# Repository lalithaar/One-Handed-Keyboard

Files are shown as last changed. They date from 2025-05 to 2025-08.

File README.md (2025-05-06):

# **One-Handed Keyboard**

> 我们收到了一封特殊的邮件。来信者的女儿在上学途中不幸遭到重型卡车碾压，右手永久失去了功能，用电脑的时候手得在键盘和鼠标之间频繁切换，打字很慢，很累。他想让我们帮他女儿做一个单手键盘。

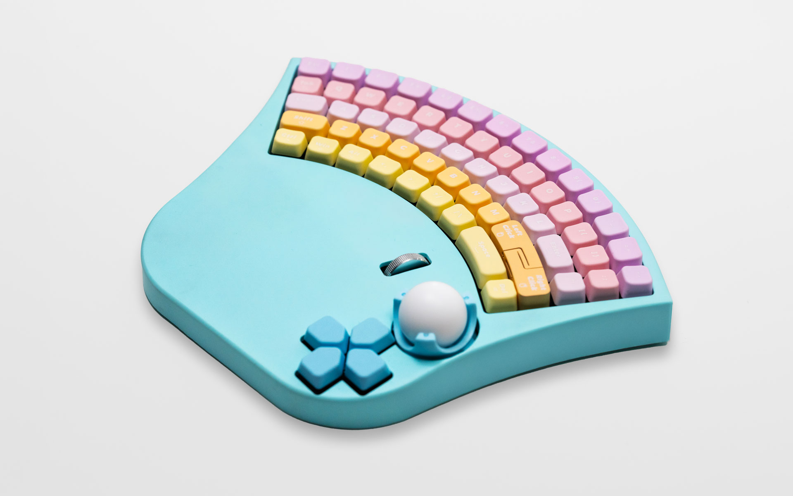
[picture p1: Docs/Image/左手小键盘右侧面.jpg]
左手小键盘


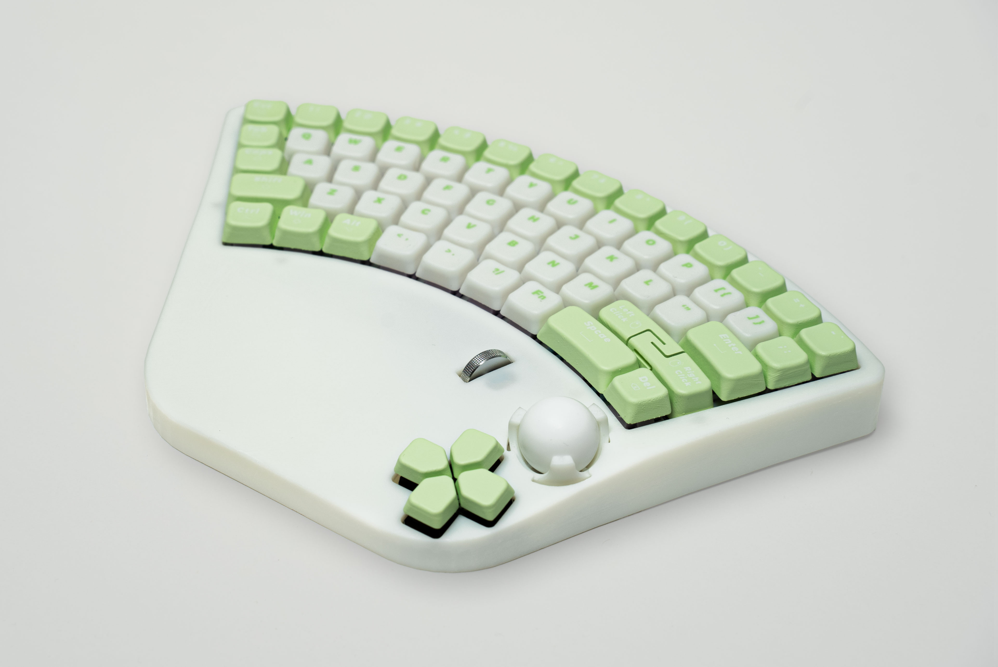
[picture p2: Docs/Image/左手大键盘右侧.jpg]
左手大键盘


这是一把单模且集成了轨迹球的机械键盘，固件使用[QMK](https://github.com/qmk/qmk_firmware)，感谢所有为 QMK 社区做出贡献的开发者。

键盘制作参考：[【何同学】我们做了个特别的键盘…](https://www.bilibili.com/video/BV1DtjAzUEb9)

硬件开源：[HTXStudio单手键盘](https://oshwhub.com/htx-studio/One-Handed_Keyboard)

[GitHub repository](https://github.com/htx-studio/One-Handed-Keyboard)

[Gitee repository](https://gitee.com/htxstudio/one-handed-keyboard)

开发环境与搭建参考[这里](https://docs.qmk.fm/newbs_getting_started "设置您的QMK环境")，固件源码在[这里](https://github.com/htx-studio/qmk_firmware/tree/master/keyboards/htx_studio)。

本仓库的资料内容包括：

* 左右手一共三款键盘的8块PCB，提供立创EDA工程。
* VIA改键配置文件，以及编译完成的固件。
* 模型设计文件。

---

## 仓库目录结构

#### Docs（文档）

芯片的数据手册与图片。

#### Firmware（固件）

三款不同型号键盘的QMK固件，以及用于VIA改键的JSON文件。

#### Hardware（硬件）

嘉立创EDA的项目文件。

#### Model（模型）

每个型号键盘使用到的模型文件，加工文件。

---

## 制作指南

### PCB：

1-右手键盘-热插拔(大)：板材FR-4，板厚1.6mm，四层板，层压结构JLC04161H-3313，阻抗管控+/-20%。

1-左手键盘-焊板(小)：板材FR-4，板厚1.6mm，双层板，ALPS黄轴插入时需稍用力安装到位。

1-左手键盘-热插拔(大)：板材FR-4，板厚1.6mm，四层板，层压结构JLC04161H-3313，阻抗管控+/-20%。

2-TypeC：板材FR-4，板厚1.6mm，双层板，标识CON1（仅适用于大键盘）。

3-轨迹球：板材FR-4，板厚1.6mm，双层板，模块需注意焊接方向，标识CON3。

4-鼠标滚轮：板材FR-4，板厚1.6mm，双层板，建议使用7mm高编码器，6mm高按键，按键触发压力≤180g，标识CON2。

5-方向按键：板材FR-4，板厚1.6mm，双层板，ALPS黄轴插入时需稍用力安装到位，标识CON4。

6-主控板-左手(小)：板材FR-4，板厚1.6mm，双层板。

> * 其中3款为键盘控制公用小板 `《3-轨迹球》《4-鼠标滚轮》《5-方向按键》`。
> * `《5-方向按键》`和 `《1-左手键盘-焊板(小)》`，按键轴使用ALPS黄轴。
> * 注意左右手大键盘并非完全镜像。
> * 轨迹球控制使用SPI1通道，滚轮有单独两条信号线，这可以使得替换其它控制设备而不需要较大的调整。
> * 主控使用 STM32G431CBU6。
> * 兼容A to C 或 C to C 数据线。

### 打印件：

键帽：树脂、PLA等。

轨迹球座：树脂、PLA等。

鼠标左右键：树脂、PLA等。

外壳：树脂、PLA等。

底座：树脂、PLA等。

### 加工：

定位板：推荐材料pom，厚1.5mm。

定位板棉条：单面留胶。

夹心棉：推荐材料poron，厚3.5mm。

轴座棉：厚2mm。

底棉：推荐材料poron，厚4mm。

硅胶垫（仅小键盘使用）：厚5mm，硬度Shore 00-10。

### 五金：

|                    | 大键盘用量（颗） | 小键盘用量（颗） |
| :----------------- | :--------------: | :--------------: |
| M3×3×4热熔铜螺母 |        8        |        8        |
| M2×2×3热熔铜螺母 |        2        |        -        |
| M2×3×3热熔铜螺母 |        17        |        12        |
| M3×6沉头螺丝      |        2        |        6        |
| M3×15沉头螺丝     |        -        |        4        |
| M3×22沉头螺丝     |        6        |        -        |
| M2×8杯头螺丝      |        4        |        4        |
| M2×3杯头螺丝      |        2        |        -        |
| M2×5杯头螺丝      |        13        |        8        |
| M3×16扁头螺丝     |        -        |        2        |

### 其它：

轨迹球：直径25mm，材质PTFE。

润滑球：直径2mm，材质PTFE，安装于打印件轨迹球座中，数量6颗。

滚轮：推荐直径19mm-20mm之间，厚4mm-5mm之间，材质金属。

卫星轴：2U钢板卫星轴。

按键轴：小键盘57颗超小ALPS黄轴，大键盘57颗常见机械轴。

排线：间距0.5mm，8P反向，10cm2条，15cm2条。

> * 控制板和小板的FPC座均有CON标识，对应接口相接。
> * 文件内使用可上下接FPC排线座，需要注意排线座均下接的情况下，使用反向排线连接。

### 模型结构：

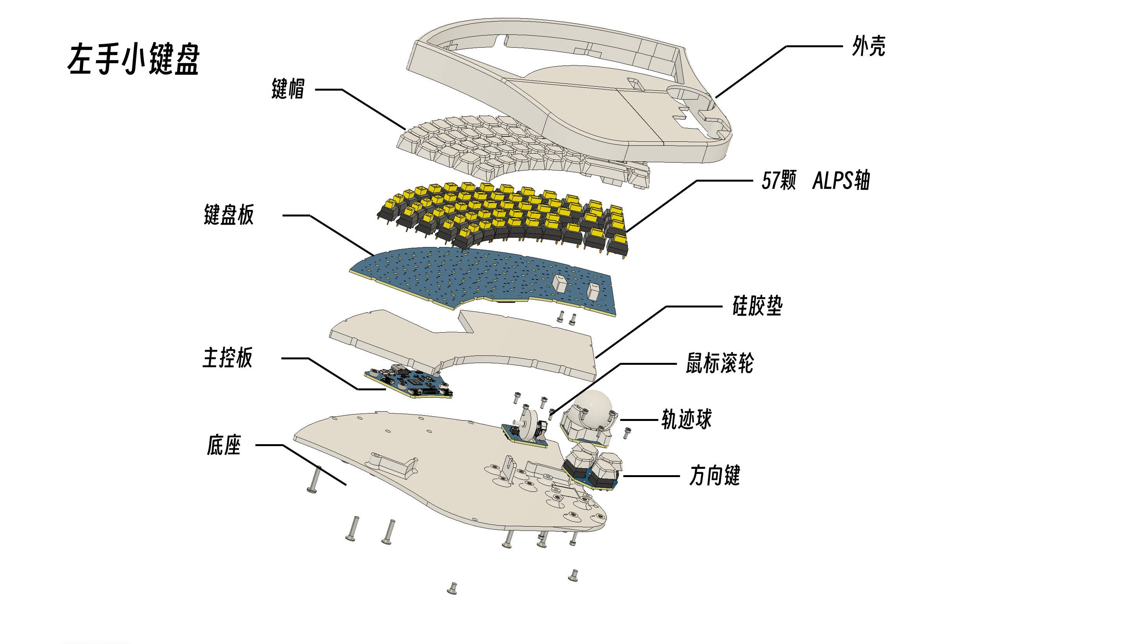
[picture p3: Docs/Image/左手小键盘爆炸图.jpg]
左手小键盘爆炸 左手小键盘爆炸图


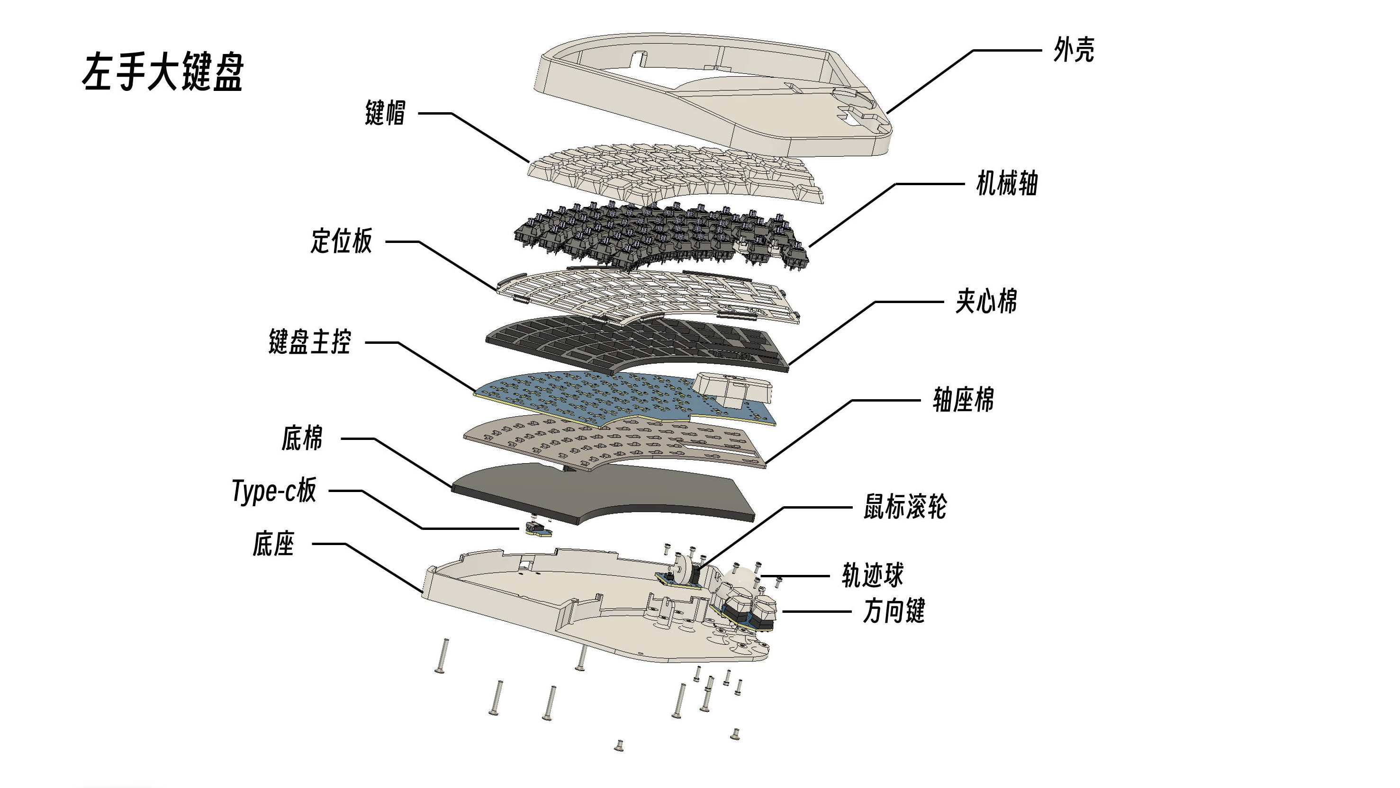
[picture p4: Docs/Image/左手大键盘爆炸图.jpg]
左手大键盘爆炸 左手大键盘爆炸图


### 安装顺序：

> 以大键盘为例

**装配前的前置工作**

* 先将4块小PCB使用排线连接至键盘本体PCB，烧录程序。
* 安装3-5个轴体，滚轮和轨迹球。装配前确保功能是正常的。
* 在打印的外壳与底座对应位置，安装正确的热熔铜螺母。
* 键帽印字。
* 将棉条贴在定位板突出部分（正反面都有）。

> 第一次烧录固件时，可以按住PCB背面标有 "B" 的按钮，再插入USB线进行固件烧录。
>
> 若更新固件可以按住键盘上的 "ESC" 键，再插入USB线进行固件烧录。
>
> 更多可以参考 [Flashing Your Keyboard (QMK)](https://docs.qmk.fm/newbs_flashing)

**接下来开始装配**

1. 将4块小板使用螺丝安装到底座对应位置（注意排线和安装方向），轨迹球座在下方安装螺丝。
2. 将左右键使用螺丝固定在键盘PCB上。
3. 从下到上以底棉、轴座棉、键盘PCB、夹心棉、定位板顺序放入底座扇形区域。
4. 插入按键轴体。
5. 放入外壳，在下方使用螺丝固定。
6. 安装键帽，完成装配。

> 螺丝螺母安装指南可以参考[这里](https://github.com/htx-studio/One-Handed-Keyboard/tree/main/Model)

最后，这是我们第一次开源项目，如果有什么不足欢迎大家批评指正，感谢大家。

---

## 引用

[Quantum Mechanical Keyboard Firmware](https://docs.qmk.fm/)

mrjohnk. ADNS-9800. [GitHub repository](https://github.com/mrjohnk/ADNS-9800/)

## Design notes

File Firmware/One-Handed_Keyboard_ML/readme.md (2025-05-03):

# One-Handed_Keyboard_ML

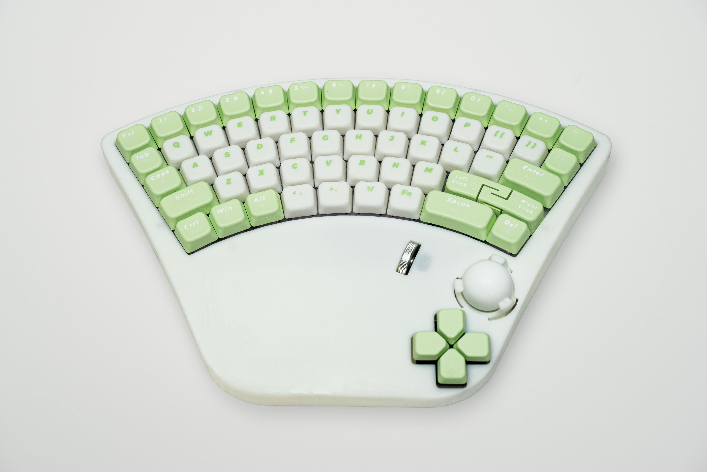
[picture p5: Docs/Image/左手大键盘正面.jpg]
左手大键盘正面


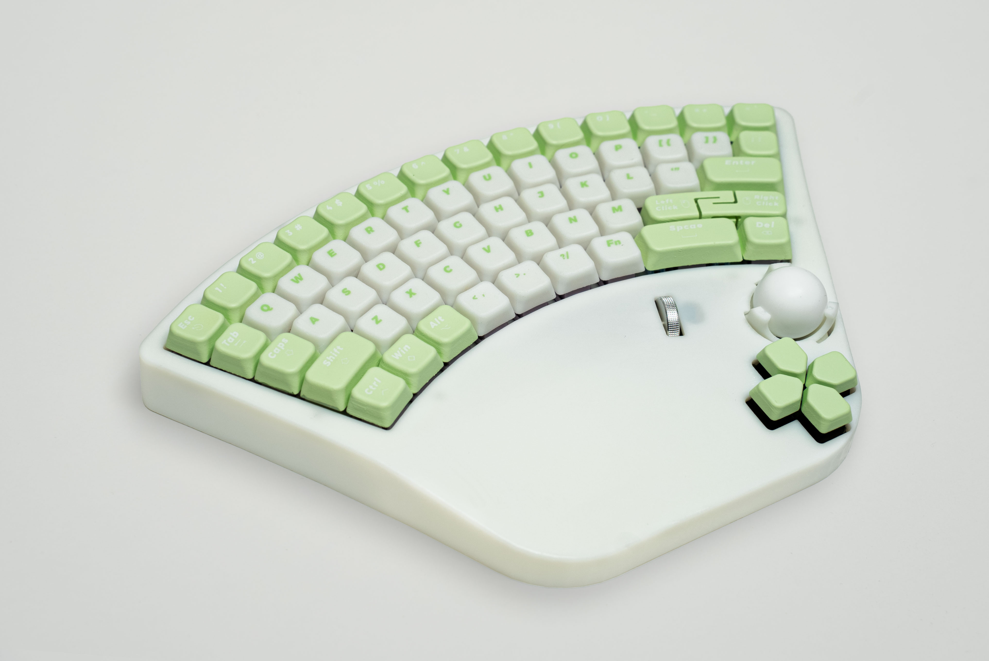
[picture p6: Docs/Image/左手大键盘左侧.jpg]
左手大键盘侧面


---

Powered by [QMK](https://docs.qmk.fm/)

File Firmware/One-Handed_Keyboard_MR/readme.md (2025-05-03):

# One-Handed_Keyboard_MR

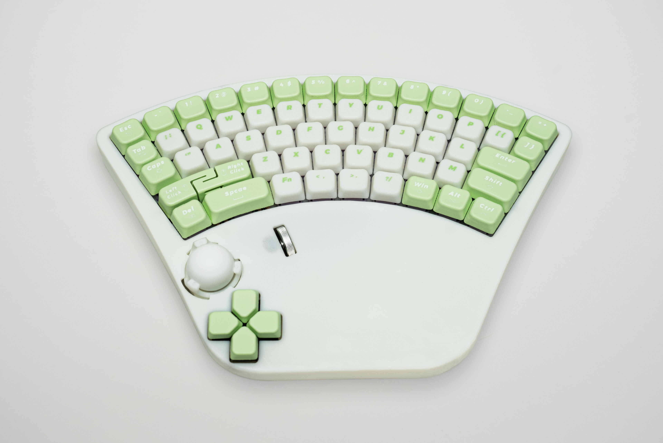
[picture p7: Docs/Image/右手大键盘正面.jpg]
右手大键盘正面


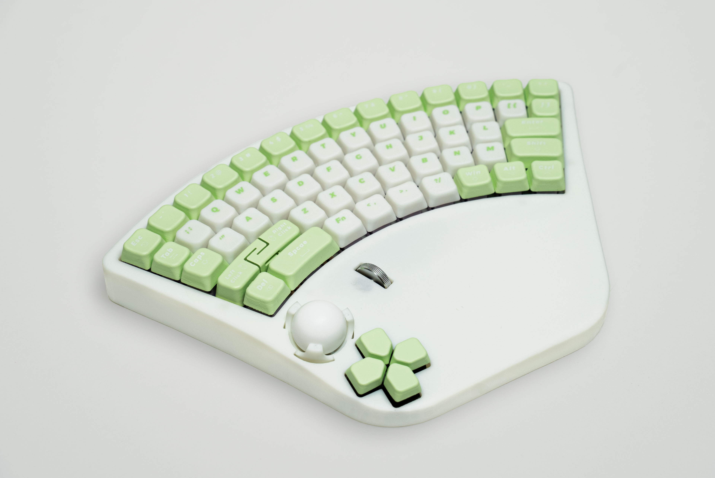
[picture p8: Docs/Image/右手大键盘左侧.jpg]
右手大键盘侧面


---

Powered by [QMK](https://docs.qmk.fm/)

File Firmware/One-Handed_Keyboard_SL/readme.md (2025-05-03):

# One-Handed_Keyboard_SL

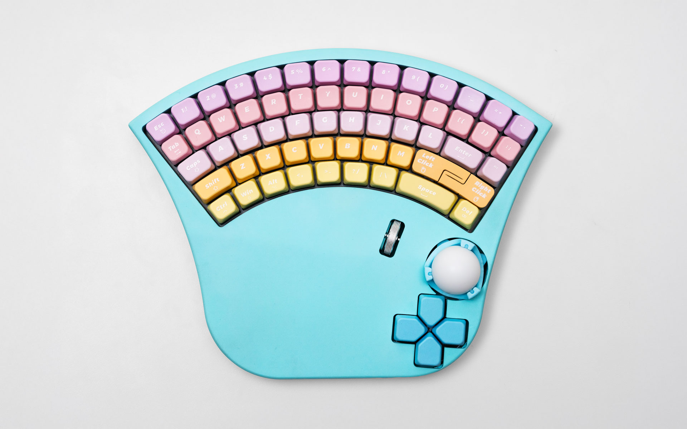
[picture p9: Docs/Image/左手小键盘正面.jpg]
左手小键盘正面


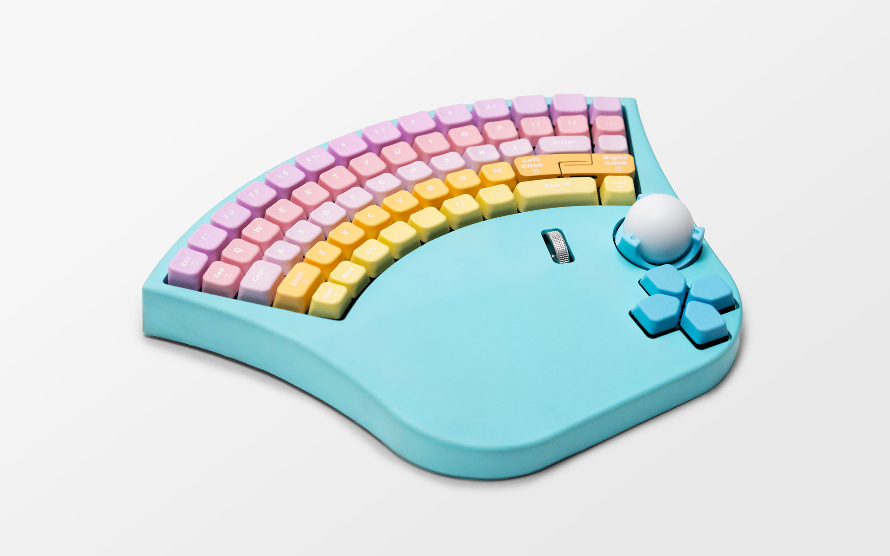
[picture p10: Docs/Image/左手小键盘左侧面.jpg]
左手小键盘侧面


---

Powered by [QMK](https://docs.qmk.fm/)

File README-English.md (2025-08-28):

# **One-Handed Keyboard**

> We received a very special email. The sender’s daughter was tragically hit by a heavy truck on her way to school and permanently lost the use of her right hand. When using a computer, she has to constantly switch between the keyboard and the mouse, making typing slow and exhausting. He asked us to help create a one-handed keyboard for her.

Left-hand small keyboard

Left-hand large keyboard

This is a single-mode mechanical keyboard with a built-in trackball. The firmware uses [QMK](https://github.com/qmk/qmk_firmware). Many thanks to all developers who contribute to the QMK community.

Keyboard inspiration: [Video by He Tongxue (Bilibili)](https://www.bilibili.com/video/BV1DtjAzUEb9)

Hardware open-source files: [HTXStudio One-Handed Keyboard](https://oshwhub.com/htx-studio/One-Handed_Keyboard)

[GitHub repository](https://github.com/htx-studio/One-Handed-Keyboard)
[Gitee repository](https://gitee.com/htxstudio/one-handed-keyboard)

Development setup guide is [here](https://docs.qmk.fm/newbs_getting_started "Set up your QMK environment"). The firmware source code is [here](https://github.com/htx-studio/qmk_firmware/tree/master/keyboards/htx_studio).

This repository contains:

* Eight PCB designs for three different keyboard models (both left- and right-handed), with LCSC EDA project files.
* VIA remapping configuration files and precompiled firmware.
* 3D model design files.

---

## Repository Structure

#### Docs (Documentation)

Datasheets and images of the chips.

#### Firmware

QMK firmware for the three keyboard models, plus VIA keymap JSON files.

#### Hardware

LCSC EDA project files.

#### Model

3D model files and machining files for each keyboard model.

---

## Build Guide

### PCB:

1. Right-hand keyboard – Hot-swappable (large): FR-4, 1.6mm thick, 4 layers, JLC04161H-3313 stackup, impedance control ±20%.
2. Left-hand keyboard – Soldered (small): FR-4, 1.6mm thick, 2 layers. ALPS yellow switches require firm pressing during installation.
3. Left-hand keyboard – Hot-swappable (large): FR-4, 1.6mm thick, 4 layers, JLC04161H-3313 stackup, impedance control ±20%.
4. Type-C daughterboard: FR-4, 1.6mm thick, 2 layers, marked CON1 (only for large keyboards).
5. Trackball module: FR-4, 1.6mm thick, 2 layers, watch soldering orientation, marked CON3.
6. Scroll wheel: FR-4, 1.6mm thick, 2 layers, recommended encoder height 7mm, button height 6mm, actuation ≤180g, marked CON2.
7. Direction keys: FR-4, 1.6mm thick, 2 layers, ALPS yellow switches require firm pressing during installation, marked CON4.
8. Main control board – Left-hand (small): FR-4, 1.6mm thick, 2 layers.

> * The three small control boards are shared across all keyboards: `3-Trackball`, `4-Scroll Wheel`, `5-Direction Keys`.
> * Both `5-Direction Keys` and `1-Left-hand Soldered (small)` use ALPS yellow switches.
> * Note: left-hand and right-hand large keyboards are not perfect mirrors.
> * Trackball uses SPI1 channel; scroll wheel uses two dedicated signal lines, allowing replacement with other devices.
> * MCU: STM32G431CBU6.
> * Compatible with both A-to-C and C-to-C cables.

### 3D-Printed Parts:

* Keycaps: resin, PLA, etc.
* Trackball mount: resin, PLA, etc.
* Mouse buttons: resin, PLA, etc.
* Case: resin, PLA, etc.
* Base: resin, PLA, etc.

### Materials:

* Positioning plate: POM, 1.5mm thick.
* Positioning plate foam strips: single-sided adhesive.
* Sandwich foam: PORON, 3.5mm thick.
* Switch pad foam: 2mm thick.
* Bottom foam: PORON, 4mm thick.
* Silicone pad (only for small keyboard): 5mm thick, Shore 00-10 hardness.

### Hardware:

| Component              | Large Keyboard | Small Keyboard |
| :--------------------- | :------------: | :------------: |
| M3×3×4 heat-set insert |        8       |        8       |
| M2×2×3 heat-set insert |        2       |        –       |
| M2×3×3 heat-set insert |       17       |       12       |
| M3×6 flat-head screw   |        2       |        6       |
| M3×15 flat-head screw  |        –       |        4       |
| M3×22 flat-head screw  |        6       |        –       |
| M2×8 button-head screw |        4       |        4       |
| M2×3 button-head screw |        2       |        –       |
| M2×5 button-head screw |       13       |        8       |
| M3×16 pan-head screw   |        –       |        2       |

### Other Components:

* Trackball: 25mm diameter, PTFE.
* Support balls: 2mm diameter, PTFE, 6 pieces installed in the printed trackball holder.
* Scroll wheel: recommended 19–20mm diameter, 4–5mm thickness, metal.
* Stabilizers: 2U plate-mount stabilizers.
* Switches:

  * Small keyboard: 57 ALPS yellow low-profile switches.
  * Large keyboard: 57 standard mechanical switches.
* Ribbon cables: 0.5mm pitch, 8-pin reverse, two at 10cm and two at 15cm.

> - All control boards and small boards have CON markings for matching connectors.
> - For FPC connectors placed on opposite sides, use reverse ribbon cables when all connectors are bottom-facing.

### Exploded Models:

Small left-hand keyboard exploded Small left-hand exploded
Large left-hand keyboard exploded Large left-hand exploded

### Assembly Order (Large Keyboard Example):

**Pre-assembly steps:**

* Connect the 4 small PCBs to the main keyboard PCB with ribbon cables, flash the firmware.
* Install 3–5 switches, scroll wheel, and trackball. Check functionality before full assembly.
* Insert heat-set inserts into the case and base.
* Print legends on keycaps.
* Stick foam strips onto positioning plate (both sides).

> For the first firmware flash, press the button labeled **“B”** on the back of the PCB while plugging in the USB cable.
> To update firmware, hold **ESC** while plugging in USB.
> See [Flashing Your Keyboard (QMK)](https://docs.qmk.fm/newbs_flashing) for details.

**Assembly steps:**

1. Fix the 4 small PCBs to the base with screws (watch cable orientation). The trackball holder is screwed from below.
2. Mount the mouse buttons on the keyboard PCB.
3. Stack layers in this order: bottom foam → switch pad foam → keyboard PCB → sandwich foam → positioning plate.
4. Insert switches.
5. Place the case on top and secure with screws.
6. Install keycaps. Assembly complete.

> Screw and insert installation guide can be found [here](https://github.com/htx-studio/One-Handed-Keyboard/tree/main/Model).

This is our first open-source project. Any feedback or suggestions are welcome. Thank you!

---

## References

[Quantum Mechanical Keyboard Firmware](https://docs.qmk.fm/)
mrjohnk. ADNS-9800. [GitHub repository](https://github.com/mrjohnk/ADNS-9800/)

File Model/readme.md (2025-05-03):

## 热熔螺母与紧固件安装指南

#### 大键盘

> 以左手大键盘为例

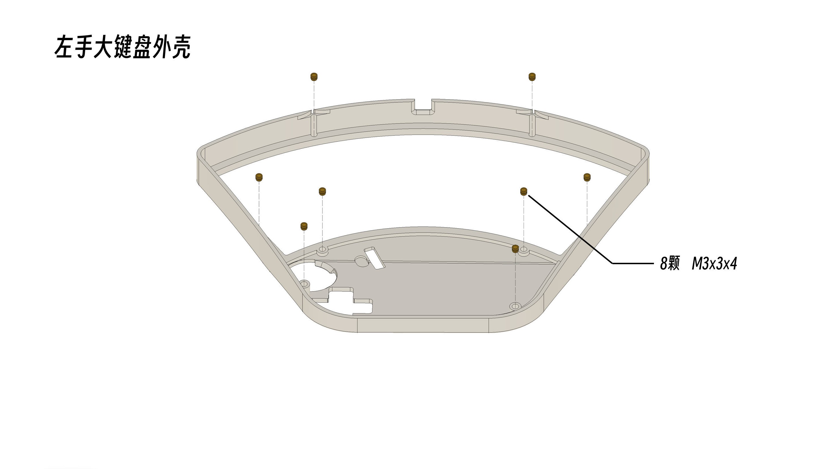
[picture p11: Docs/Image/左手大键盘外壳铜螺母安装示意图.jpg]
左手大键盘外壳铜螺母安装示意图


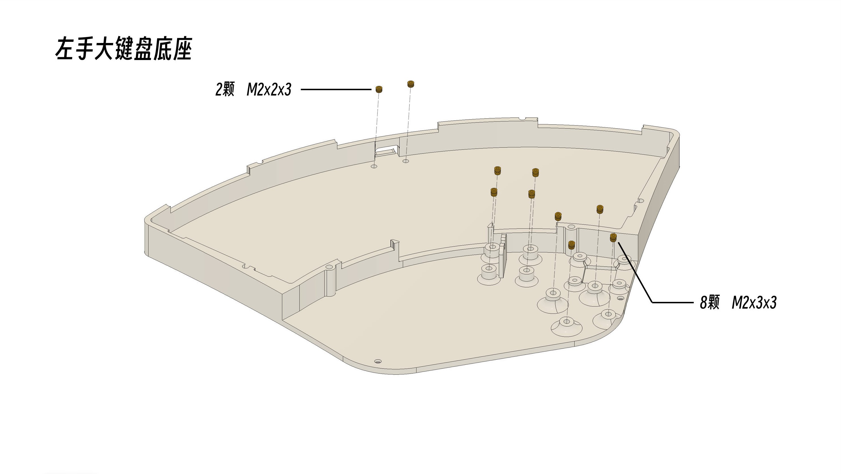
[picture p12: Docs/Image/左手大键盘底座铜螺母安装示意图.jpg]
左手大键盘底座铜螺母安装示意图


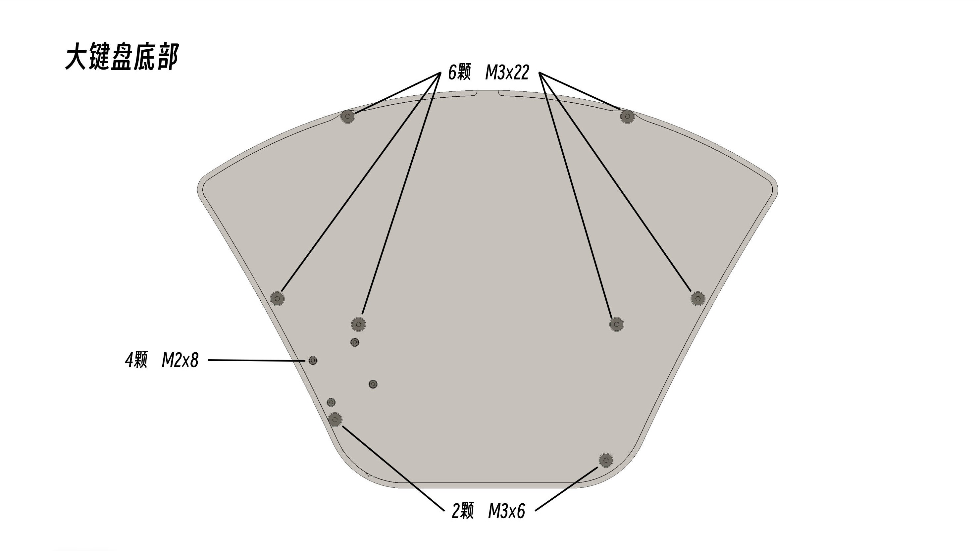
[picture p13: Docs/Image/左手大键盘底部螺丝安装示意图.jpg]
左手大键盘底部螺丝安装示意图


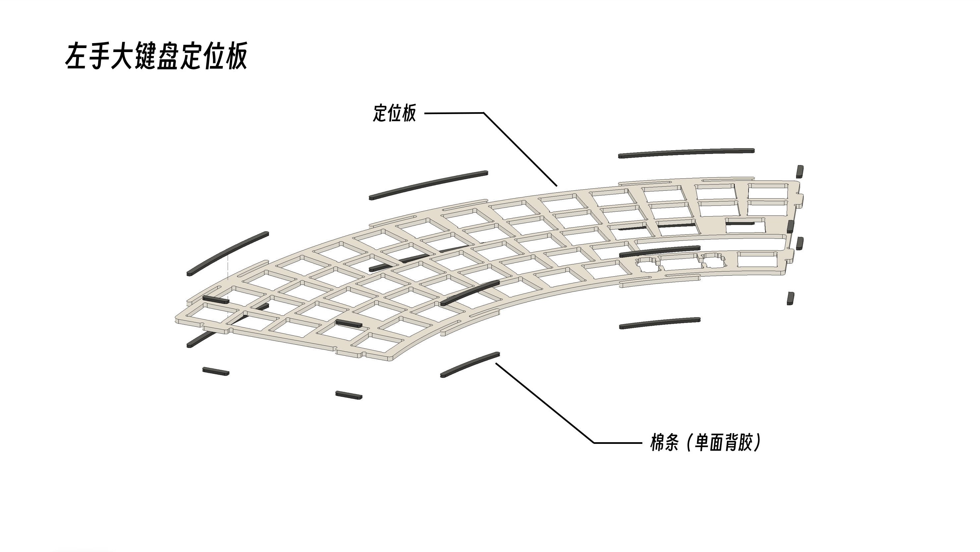
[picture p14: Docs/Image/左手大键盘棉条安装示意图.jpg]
左手大键盘棉条安装示意图


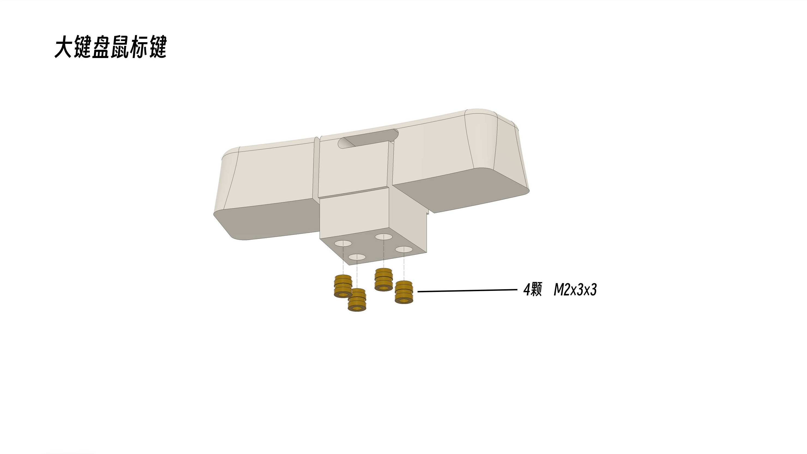
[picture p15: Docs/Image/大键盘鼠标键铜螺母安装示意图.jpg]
大键盘鼠标键铜螺母安装示意图


#### 小键盘

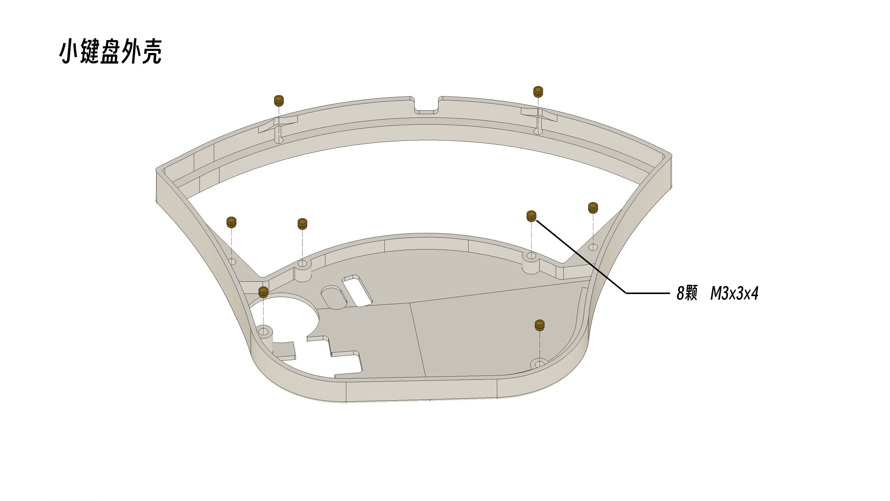
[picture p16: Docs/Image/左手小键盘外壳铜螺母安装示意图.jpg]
左手小键盘外壳铜螺母安装示意图


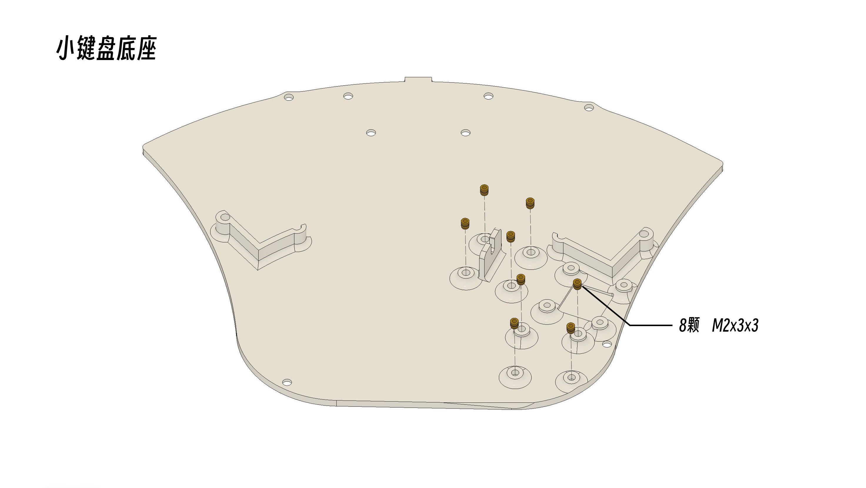
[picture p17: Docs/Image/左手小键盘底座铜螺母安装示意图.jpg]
左手小键盘底座铜螺母安装示意图


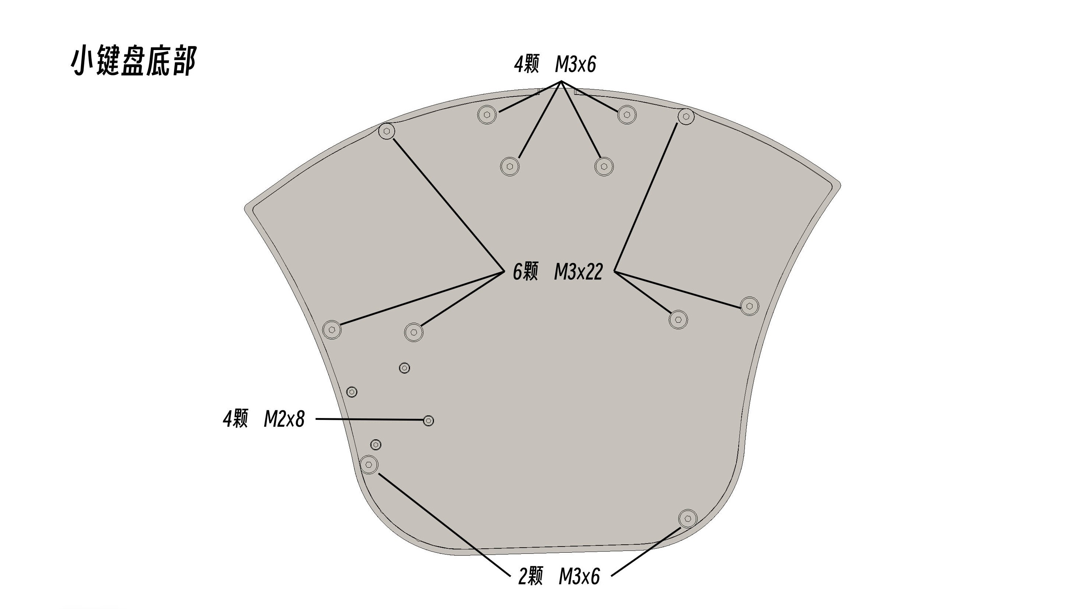
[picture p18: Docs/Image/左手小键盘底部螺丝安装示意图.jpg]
左手小键盘底部螺丝安装示意图


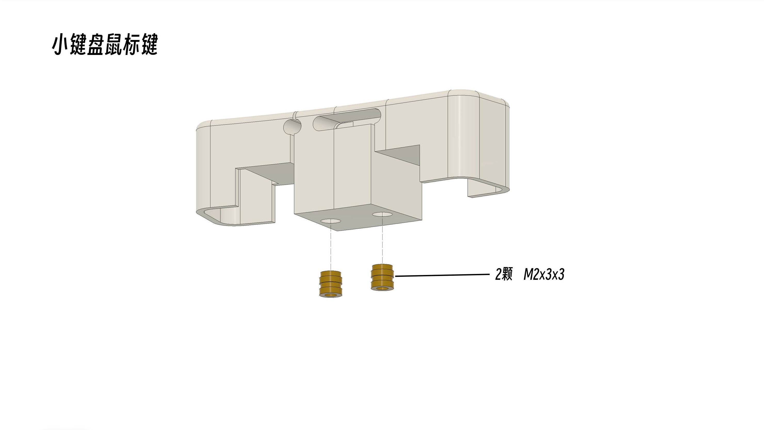
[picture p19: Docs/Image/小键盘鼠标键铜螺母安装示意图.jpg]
小键盘鼠标键铜螺母安装示意图


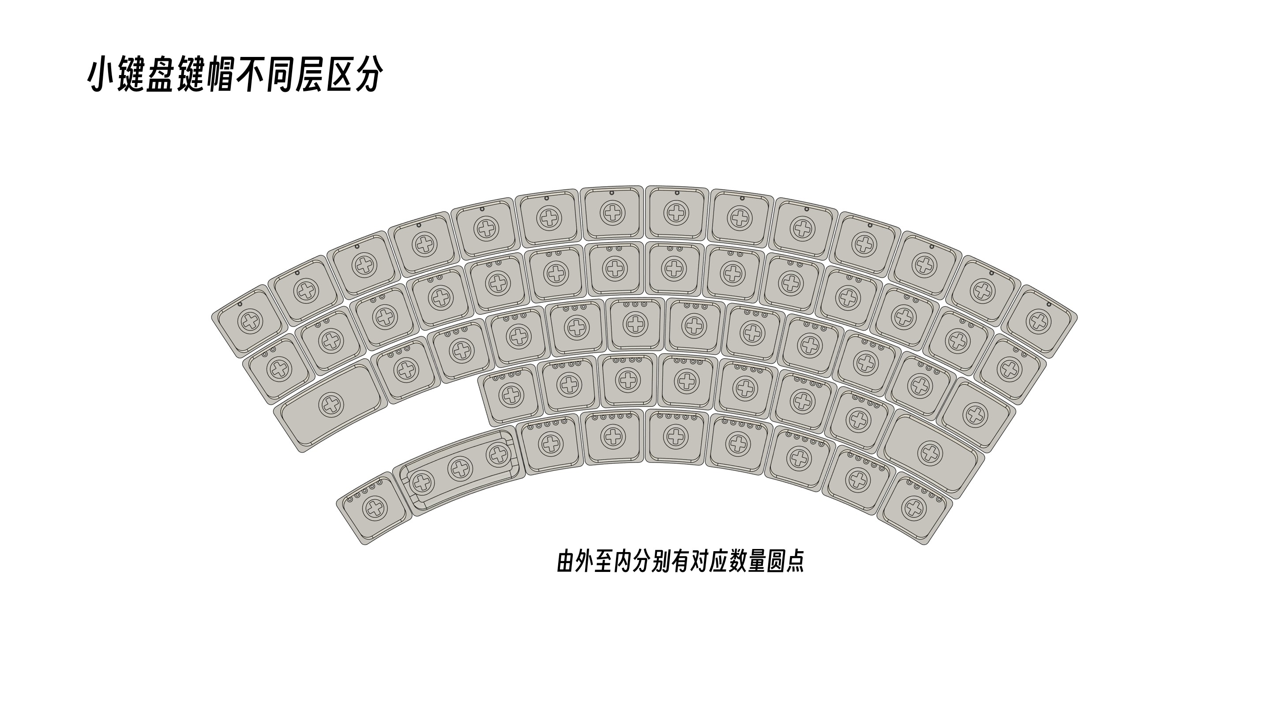
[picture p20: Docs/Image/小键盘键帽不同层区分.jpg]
小键盘键帽不同层区分


> 小键盘与大键盘键帽区分方式相同

#### 其它

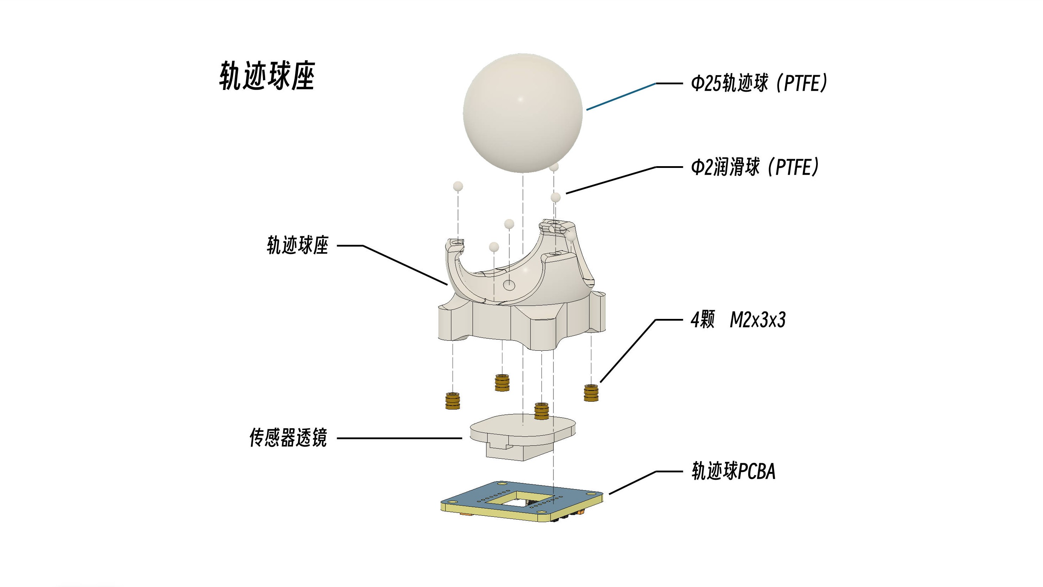
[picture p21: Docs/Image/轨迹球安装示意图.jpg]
轨迹球安装示意图


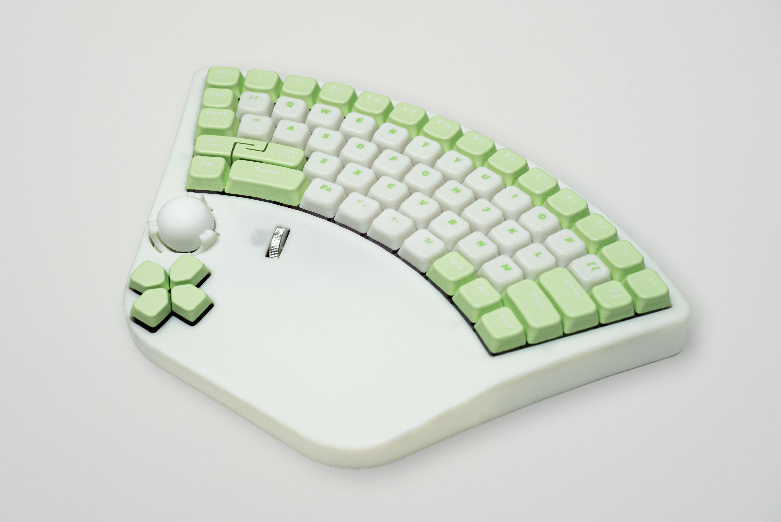
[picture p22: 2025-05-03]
Docs/Image/右手大键盘右侧.jpg

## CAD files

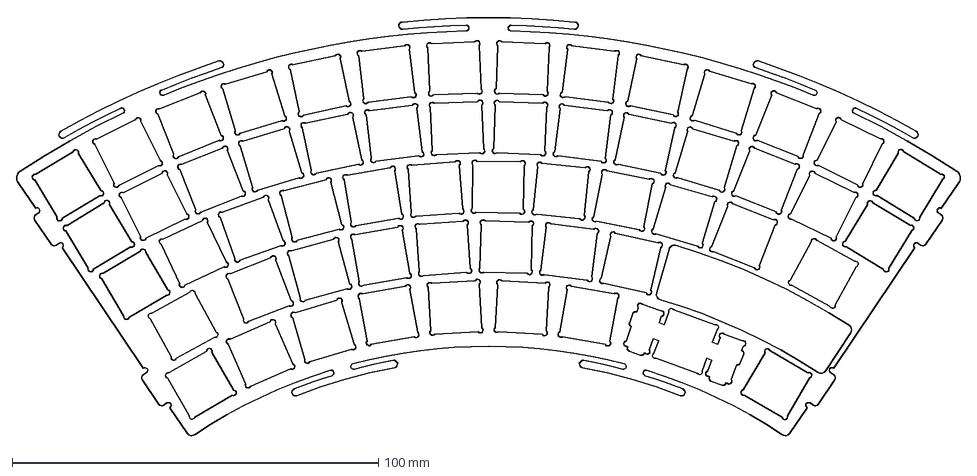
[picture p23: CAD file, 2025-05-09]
Model/One-Handed_Keyboard_ML/定位板_左.DXF
258.0 x 114.6 mm

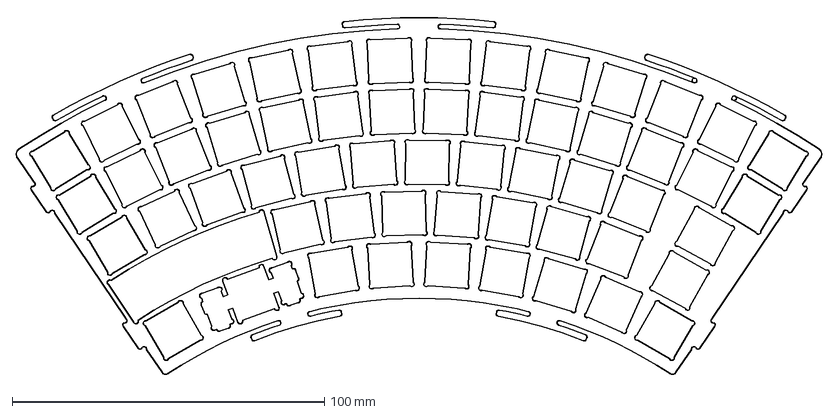
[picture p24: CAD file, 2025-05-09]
Model/One-Handed_Keyboard_MR/定位板_右.DXF
258.0 x 114.6 mm

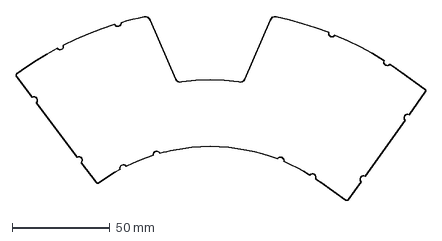
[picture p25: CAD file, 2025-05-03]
Model/One-Handed_Keyboard_SL/硅胶垫.DXF
210.0 x 94.5 mm

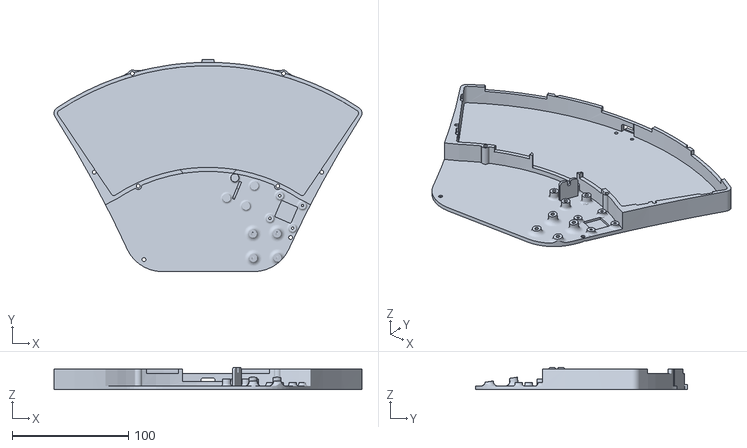
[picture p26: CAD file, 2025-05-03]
Model/One-Handed_Keyboard_ML/底座_左.STL
264.7 x 182.5 x 19.0

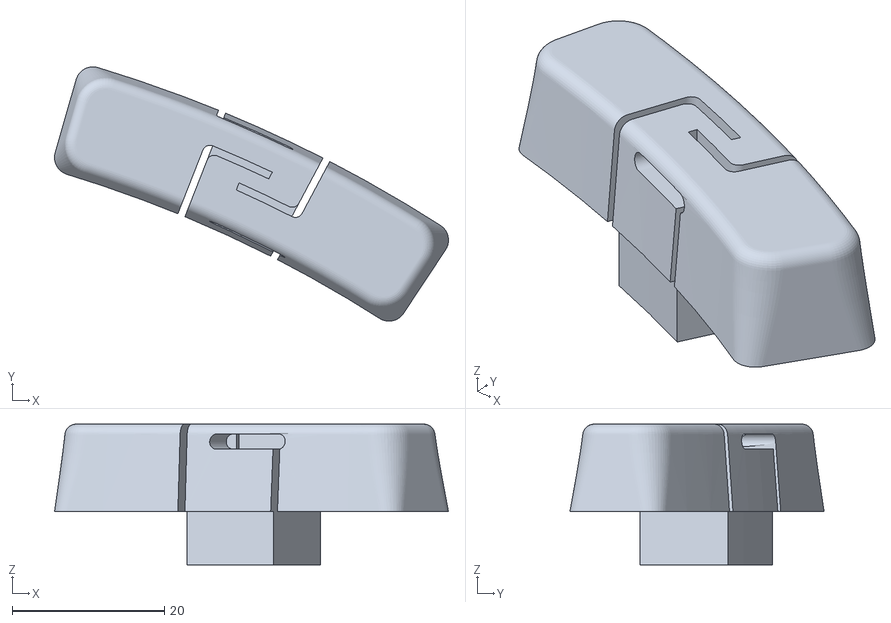
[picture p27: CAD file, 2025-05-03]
Model/One-Handed_Keyboard_MR/左右键.STL
51.8 x 33.4 x 18.5

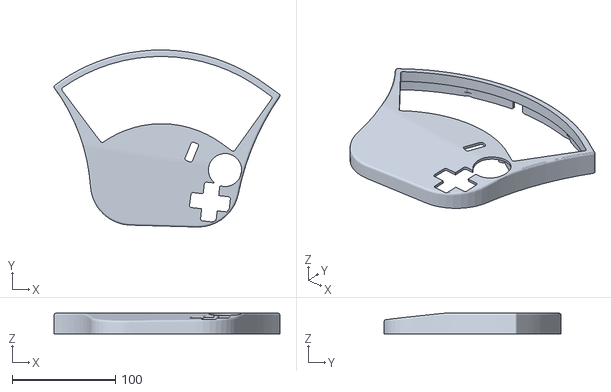
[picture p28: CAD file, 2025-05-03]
Model/One-Handed_Keyboard_SL/外壳.STL
218.6 x 171.2 x 20.0

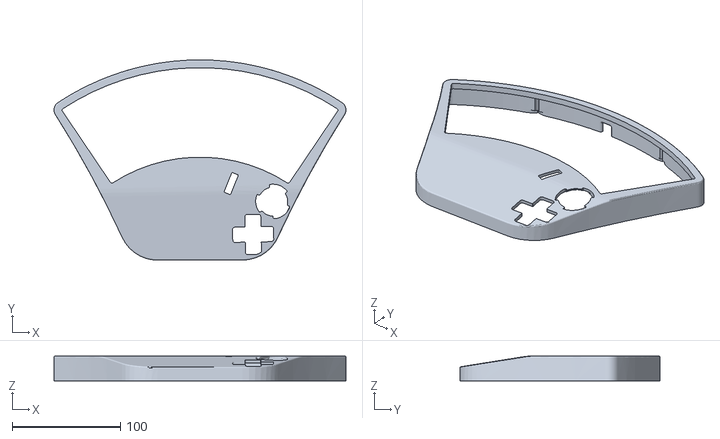
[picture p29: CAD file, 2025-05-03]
Model/One-Handed_Keyboard_ML/外壳_左.STL
269.8 x 185.0 x 23.0

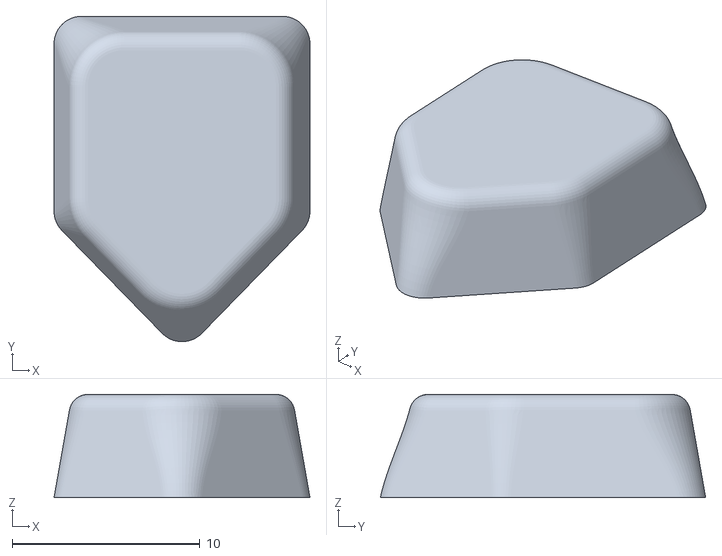
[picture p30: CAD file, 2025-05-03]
Model/One-Handed_Keyboard_MR/方向键键帽.STL
13.6 x 17.3 x 5.50

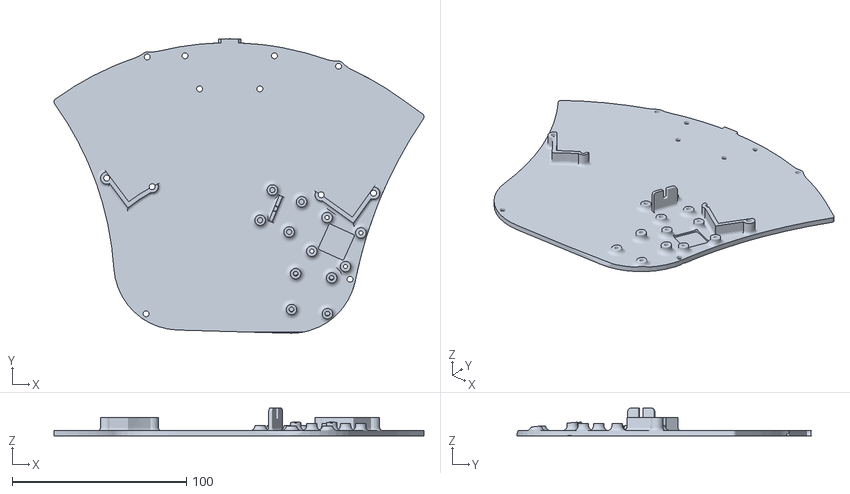
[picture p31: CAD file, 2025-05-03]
Model/One-Handed_Keyboard_SL/底座.STL
212.2 x 168.9 x 16.0

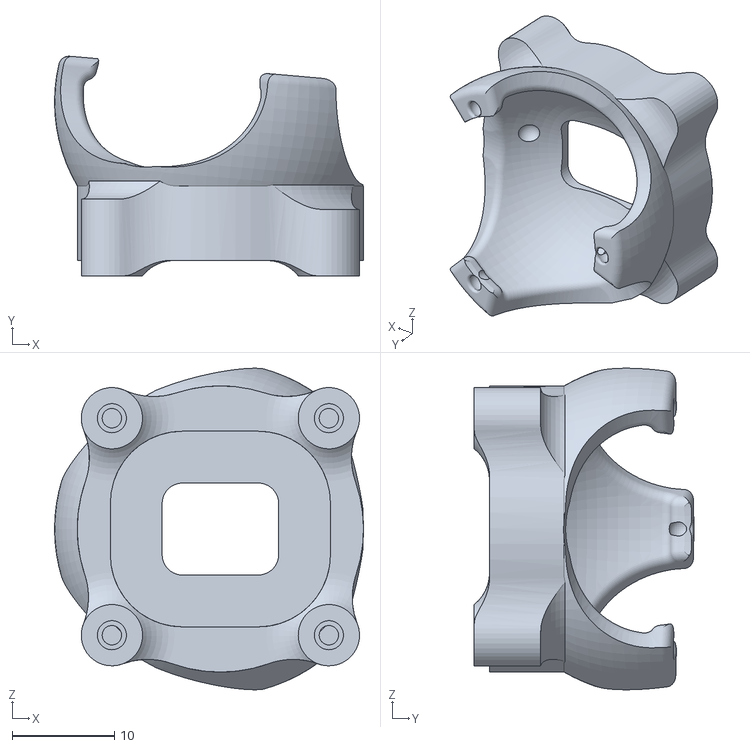
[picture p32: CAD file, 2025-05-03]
Model/One-Handed_Keyboard_ML/轨迹球座.STL
30.2 x 21.5 x 31.5

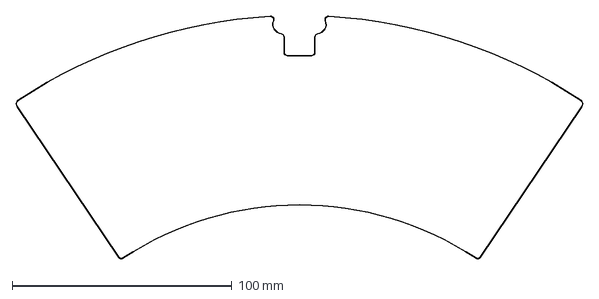
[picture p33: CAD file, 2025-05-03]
Model/One-Handed_Keyboard_MR/底棉.DXF
258.0 x 110.4 mm

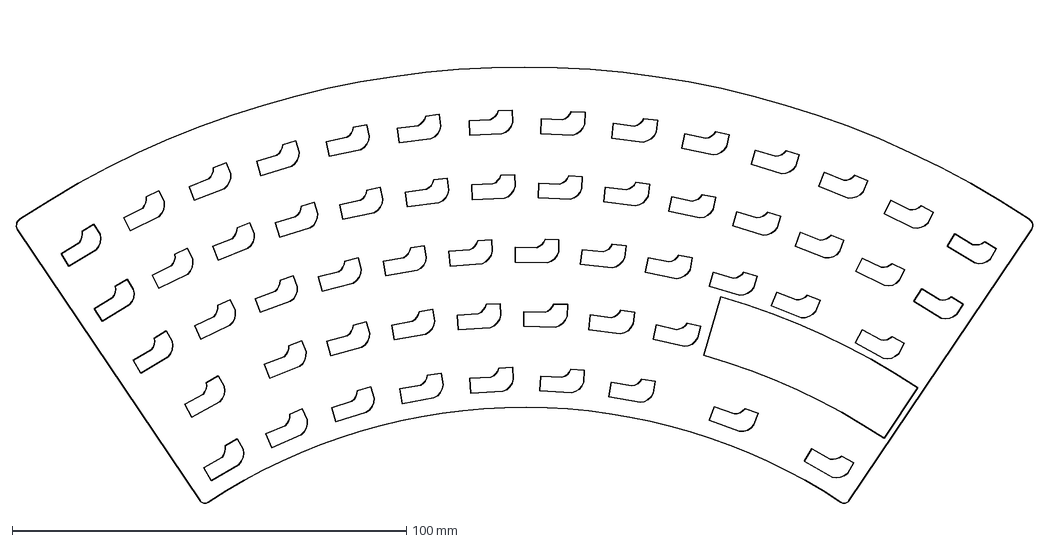
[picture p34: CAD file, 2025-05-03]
Model/One-Handed_Keyboard_ML/轴座棉_左.DXF
258.0 x 123.6 mm

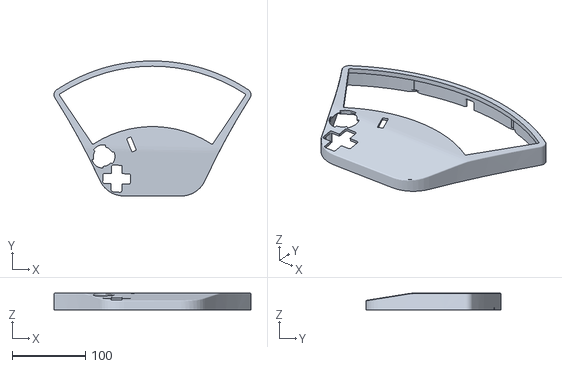
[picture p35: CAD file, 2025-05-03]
Model/One-Handed_Keyboard_MR/外壳_右.STL
269.8 x 185.0 x 23.0

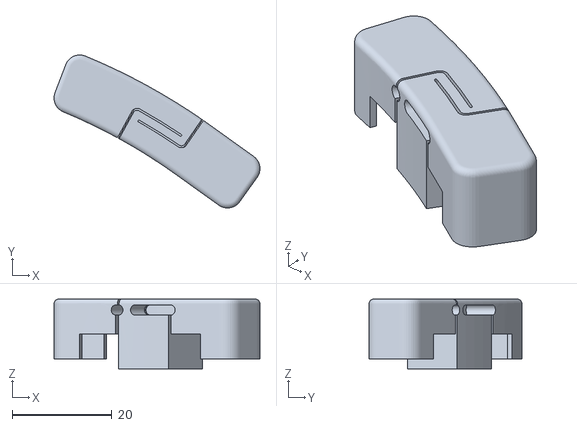
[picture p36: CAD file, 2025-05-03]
Model/One-Handed_Keyboard_SL/左右键.STL
41.2 x 30.6 x 14.0

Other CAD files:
Model/One-Handed_Keyboard_ML/夹心棉_左.DXF
Model/One-Handed_Keyboard_ML/定位板上下棉条.DXF
Model/One-Handed_Keyboard_MR/夹心棉_右.DXF
Model/One-Handed_Keyboard_MR/定位板上下棉条.DXF
Model/One-Handed_Keyboard_MR/底座_右.STL
Model/One-Handed_Keyboard_MR/轴座棉_右.DXF

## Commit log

2025-05-07 Fixed PCB via parameters
2025-05-09 Fixed the plate defect
    [定位板_右.DXF, 定位板_左.DXF]
2025-08-28 Add README for One-Handed Keyboard project
    Added detailed documentation for the One-Handed Keyboard project, including build guides, hardware specifications, and assembly instructions.
